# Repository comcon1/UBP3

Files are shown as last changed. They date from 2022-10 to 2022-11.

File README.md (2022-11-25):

# Universal Biopotential Amplifier - UBP3

Wideband multichannel differential amplifier with modular design and adjustable analogous commutation.

## Project video

Video presentation of the project (https://www.youtube.com/watch?v=Itqa7mGAqyA)

## Technical characteristics

- Input power: -15, 0, +15 V
- Type: differential
- Input resistance: 1 GOhm
- Noise level at connected inputs:
  - < 0.15 mkV (at 0.3-150 Hz)
  - < 0.8 mkV (at 0.3-1000 Hz)
- Gain coefficient:
  - Input cascade: 1, 10
  - Output cascade: 3, 10, 30, 100, 300, 1000
- Filtering:
  - Intensity: 12 dB/octave
  - LowPass: 35, 70, 150, 300, 1000, 2000, 5000, 10000, 20000 Hz 
  - HighPass: 0.1, 0.3, 1, 5, 20, 100, 300 Hz
- Output range: -5V - +5V

# Project structure

The amplifier is composed of two boards: **InputAmp** and **FilterAmp**. 

## InputAmp

Input gain board performs initial commutation of the bipolar signal with reference monopolar input and calibration signal. Next the board amplifies the signal current with 1x/10x gain.

Corresponding directory contains the complete KiCAD project including scheme and PCB.

## FilterAmp

Preamplified signal is then further amplified inside this board and undergo LowPass and HighPass filtration.

Corresponding directory contains the complete KiCAD project including scheme and PCB.

## Calibrator

Calibrator gets 0/+5V input unipolar source and gives 30/300 Hz of 1/0.1 mV square pulse unipolar signal for feeding the amplifier.

Corresponding directory contains the complete KiCAD project including scheme and PCB.

# Arrangement

Boards are designed for further geometrical stacking as shown at the how-to-assembly scheme:

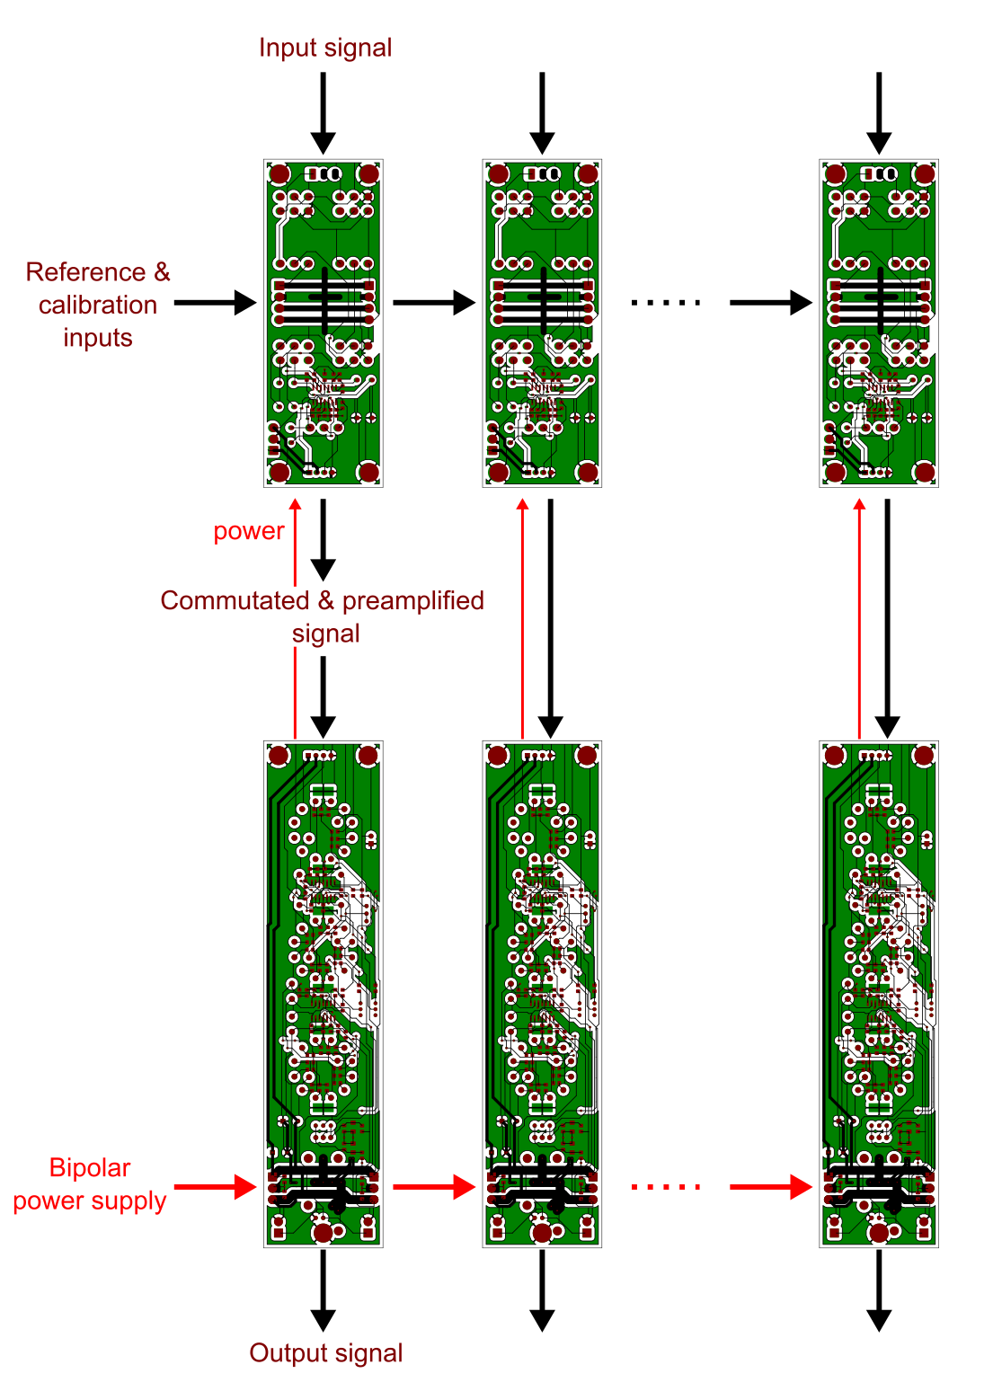
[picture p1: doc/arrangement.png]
How boards are assemblied


# History

The prototype of this amplifier was firstly used by Ilya Kuzmin and colleagues for recording ECG of rats on a tredban:

- Tarasova OS, Borzykh AA, Kuz'min IV, et al. [Dynamics of heart rate changes in rats following stepwise change of treadmill running speed]. Ross Fiziol Zh Im I M Sechenova. 2012; 98(11):1372-9.

Now it is used by Georgy Nikolaev and his students for recording EEG in the research of audiogenic epilepsy on rat model:

- Fedotova IB, Surina NM, Nikolaev GM, Revishchin AV, Poletaeva II. Rodent Brain Pathology, Audiogenic Epilepsy. Biomedicines. 2021; 9(11):1641. https://doi.org/10.3390/biomedicines9111641

# Licensing 

The project "Universal Biopotential Amplifier" 
(I. Kuzmin @kuzmin-ilya, A. Nesterenko @comcon1, G. Nikolaev)  
is released under  license CC BY-SA 3.0.

Submodules listed as independent projects are not part of this project and 
are released under their own licenses.

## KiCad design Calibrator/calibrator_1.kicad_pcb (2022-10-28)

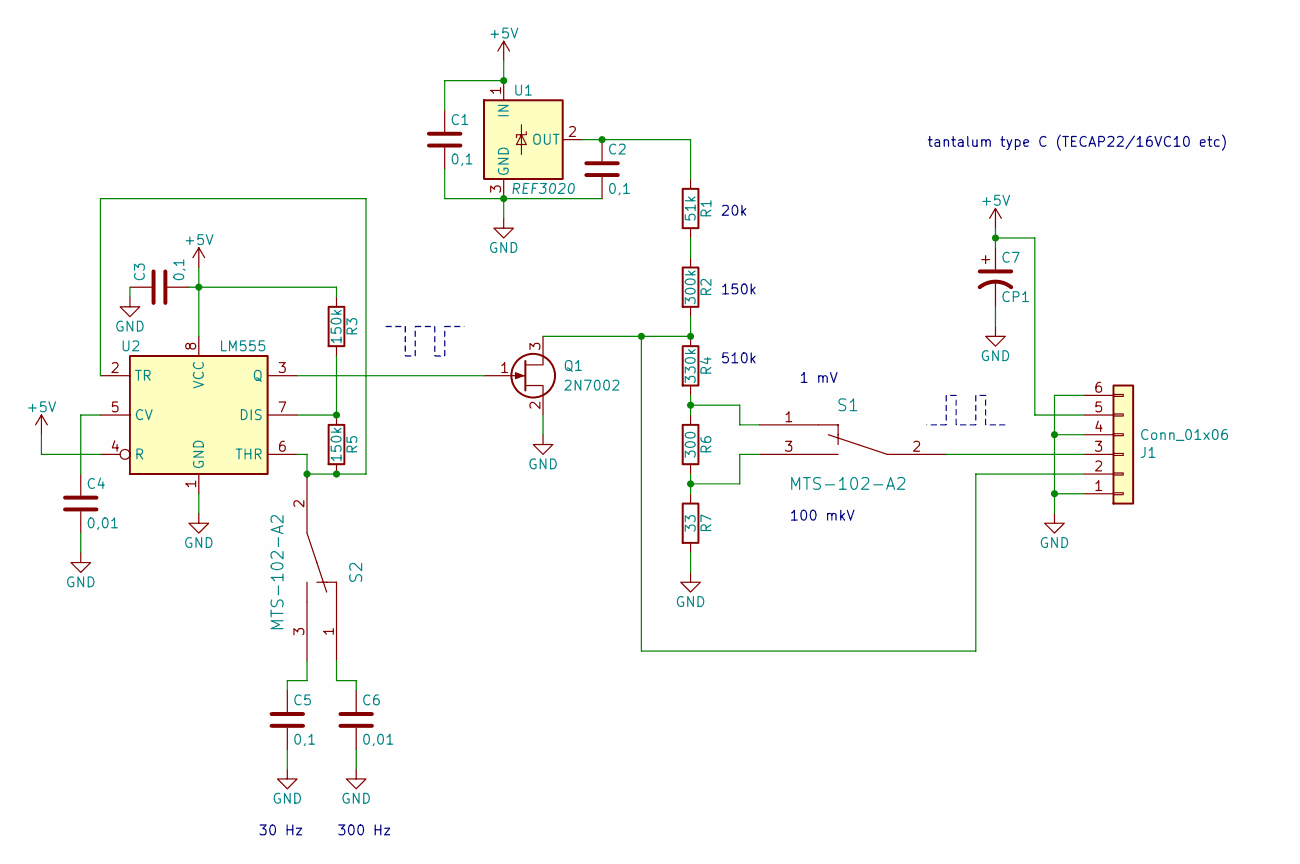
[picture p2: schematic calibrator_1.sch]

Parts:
C1, C2, C3, C5: 0,1; C_0805_2012Metric_Pad1.15x1.40mm_HandSolder
C4, C6: 0,01; C_0805_2012Metric_Pad1.15x1.40mm_HandSolder
C7: CP1; CP_EIA-6032-28_Kemet-C_Pad2.25x2.35mm_HandSolder
J1: Conn_01x06; PinHeader_1x06_P2.54mm_Horizontal
Q1: 2N7002; SOT-23_Handsoldering
R1: 51k; R_0805_2012Metric_Pad1.15x1.40mm_HandSolder
R2: 300k; R_0805_2012Metric_Pad1.15x1.40mm_HandSolder
R3, R5: 150k; R_0805_2012Metric_Pad1.15x1.40mm_HandSolder
R4: 330k; R_0805_2012Metric_Pad1.15x1.40mm_HandSolder
R6: 300; R_0805_2012Metric_Pad1.15x1.40mm_HandSolder
R7: 33; R_0805_2012Metric_Pad1.15x1.40mm_HandSolder
S1, S2: MTS-102-A2
U1: REF3020; SOT-23_Handsoldering
U2: LM555; SOIC-8_3.9x4.9mm_P1.27mm

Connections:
+5V: C1.1, C3.2, C7.1, J1.5, R3.1, U1.1 (IN), U2.4 (R), U2.8 (VCC)
GND: C1.2, C2.2, C3.1, C4.2, C5.2, C6.2, C7.2, J1.1, J1.4, J1.6, Q1.2 (S), R7.2, U1.3 (GND), U2.1 (GND)
unnamed: C2.1, R1.1, U1.2 (OUT)
unnamed: C4.1, U2.5 (CV)
unnamed: C5.1, S2.3
unnamed: C6.1, S2.1
unnamed: J1.2, Q1.3 (D), R2.2, R4.1
unnamed: J1.3, S1.2
unnamed: Q1.1 (G), U2.3 (Q)
unnamed: R1.2, R2.1
unnamed: R3.2, R5.1, U2.7 (DIS)
unnamed: R4.2, R6.1, S1.1
unnamed: R5.2, S2.2, U2.2 (TR), U2.6 (THR)
unnamed: R6.2, R7.1, S1.3

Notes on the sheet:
30 Hz
300 Hz
1 mV
100 mkV
tantalum type C (TECAP22/16VC10 etc)
510k
150k
20k

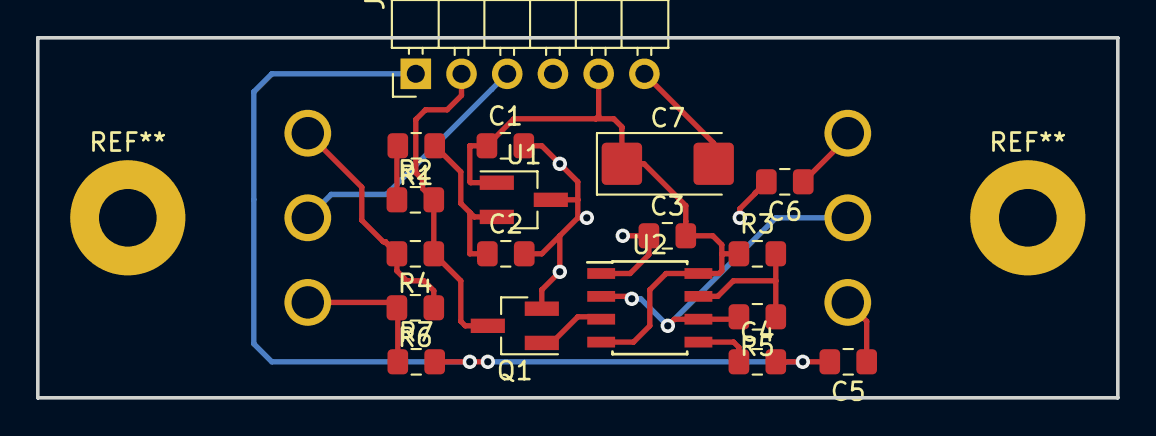
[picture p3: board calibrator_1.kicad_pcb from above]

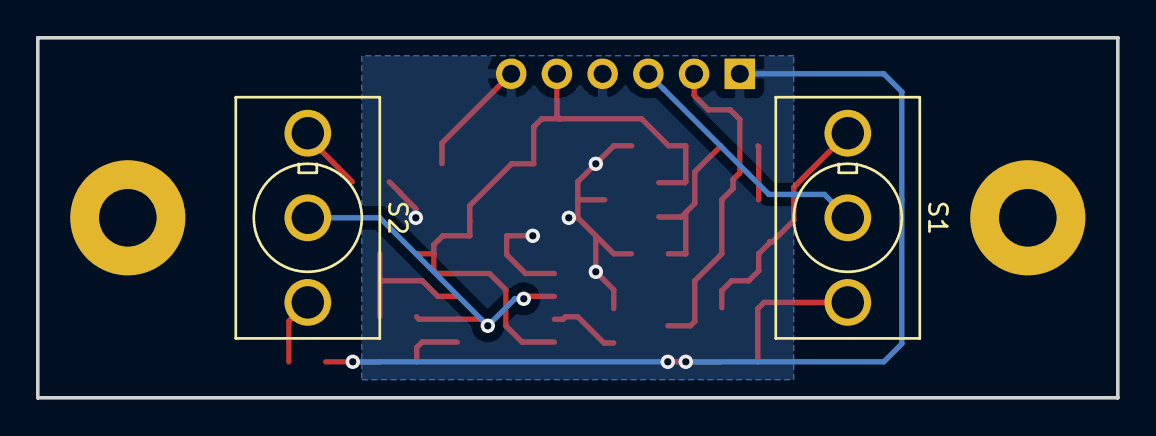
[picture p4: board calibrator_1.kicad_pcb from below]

Board: 2 copper layers, 60.0 x 20.0 mm, 20 parts (2 on the bottom side), 14 nets.

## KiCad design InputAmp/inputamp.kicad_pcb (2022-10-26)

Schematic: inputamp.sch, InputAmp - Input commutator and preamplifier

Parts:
C1, C2, C5: 1,0; C_Rect_L7.5mm_W6.5mm_P5.00mm
C3, C4: 0,1; C_0805_2012Metric_Pad1.18x1.45mm_HandSolder
J1: Conn_01x04; PinHeader_1x04_P2.54mm_Vertical
J2: Conn_01x03; PhoenixContact_MCV_1,5_3-G-3.81_1x03_P3.81mm_Vertical
J3, J5: Conn_01x04; SolderWirePad_1x04_P3.81mm_Drill1.2mm
J4: Conn_01x03; SolderWirePad_1x03_P3.81mm_Drill1.2mm
R1, R2: 20M; R_Axial_DIN0309_L9.0mm_D3.2mm_P12.70mm_Horizontal
R3: 7,5k; R_0805_2012Metric_Pad1.20x1.40mm_HandSolder
R4, R5, R6, R7, R8, R9: 30k; R_0805_2012Metric_Pad1.20x1.40mm_HandSolder
R10: 2M; R_0805_2012Metric_Pad1.20x1.40mm_HandSolder
R11: 33k; R_0805_2012Metric_Pad1.20x1.40mm_HandSolder
R12: 300k; R_0805_2012Metric_Pad1.20x1.40mm_HandSolder
SW1, SW2: MTS-202-A2; MTS-202-A2_odd_even
SW3, SW5, SW6: MTS-102-A2
SW4, SW7: MTS-212-A2; MTS-202-A2_odd_even
U1: TLC2274; SOIC-14_3.9x8.7mm_P1.27mm

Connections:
+5V: C3.2, J1.1, J4.1, U1.4
-5V: C4.2, J1.2, J4.3, U1.11
GND: C3.1, C4.1, J1.4, J2.2, J3.2, J4.2, J5.2, R1.2, R2.2, R8.2, R10.2, R11.2, SW1.5 (C), SW4.5 (C), SW7.6 (C)
unnamed: C1.1, R1.1, SW2.3 (B), U1.3
unnamed: C1.2, SW1.3 (B), SW2.1 (A)
unnamed: C2.1, R2.1, SW2.4 (B), U1.5
unnamed: C2.2, SW1.4 (B), SW2.2 (A)
unnamed: C5.1, R10.1, U1.12
unnamed: C5.2, R9.1, SW3.1, U1.8
unnamed: J1.3, SW3.2
unnamed: J2.1, SW7.2 (A)
unnamed: J2.3, SW4.1 (A)
unnamed: J3.1, J5.1, SW5.3, SW6.3
unnamed: J3.3, J5.3, SW1.6 (C)
unnamed: J3.4, J5.4, SW4.4 (B), SW7.3 (B)
unnamed: R3.1, R4.2, U1.2
unnamed: R3.2, R5.2, U1.6
unnamed: R4.1, R6.2, U1.1
unnamed: R5.1, R7.2, U1.7
unnamed: R6.1, R9.2, U1.9
unnamed: R7.1, R8.1, U1.10
unnamed: R11.1, R12.2, U1.13
unnamed: R12.1, SW3.3, U1.14
unnamed: SW1.1 (A), SW5.2
unnamed: SW1.2 (A), SW6.2
unnamed: SW4.3 (B), SW6.1, SW7.5 (C)
unnamed: SW4.6 (C), SW5.1, SW7.4 (B)

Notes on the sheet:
x10
CAL
ShieldGND
C1, C2, C5 - Epcos B32529C0105K000
Output connector (to "filteramp" block)
Reserve connector to supply power for input devices
Signal input connector
IN- GND IN+
LowPass frequency is about 0.1 Hz
SIG_OUT GND
REF
Rin
CAL_R
"CAL_R": to the +1V output of the calibrator through 1 MOhm "CAL": directly to the +1mV output of the calibrator "REF": when the circuite works in a stack, one of the inputs (called REF) is connected to all boards and may replace + or - inputs "ShieldGND": connect the shield of REF wire and DON'T c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
Connect to J5 of the next board in a stack. DON'T connect ShieldGND between boards!

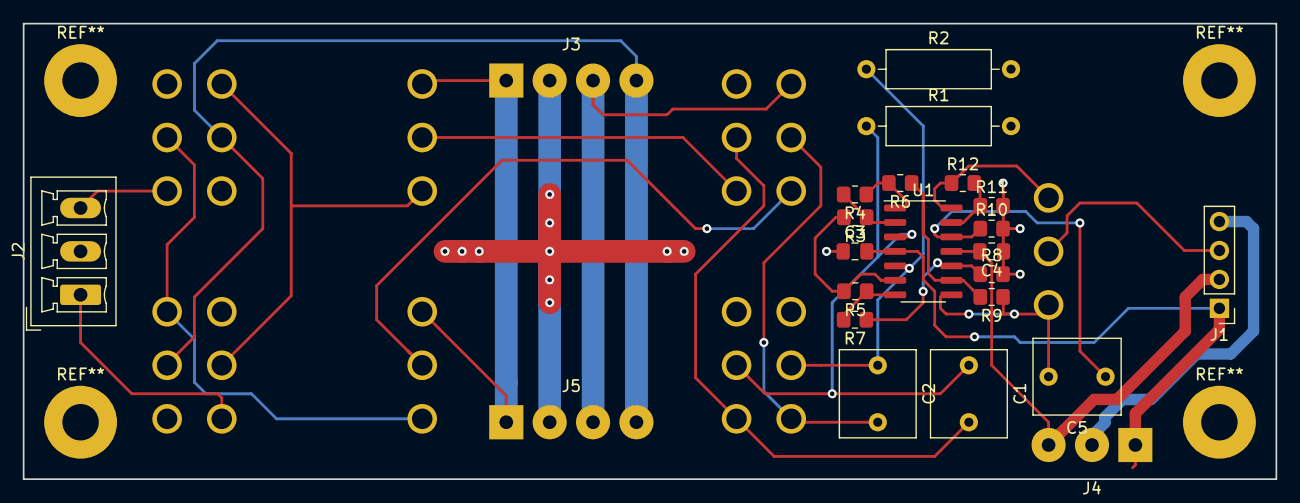
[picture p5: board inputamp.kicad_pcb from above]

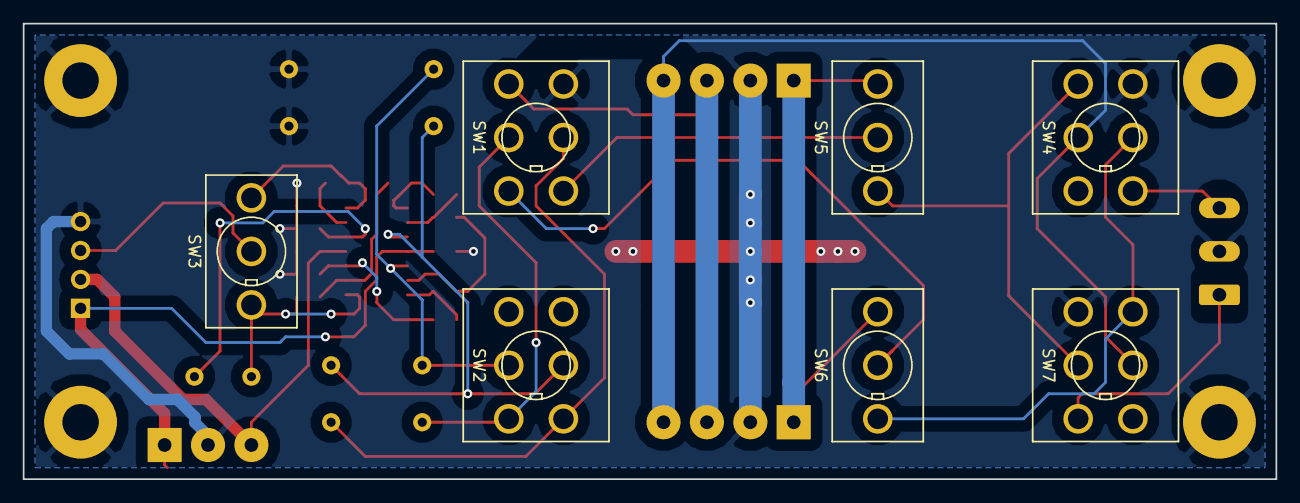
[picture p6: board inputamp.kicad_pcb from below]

Board: 2 copper layers, 110.0 x 40.0 mm, 30 parts (7 on the bottom side), 27 nets.

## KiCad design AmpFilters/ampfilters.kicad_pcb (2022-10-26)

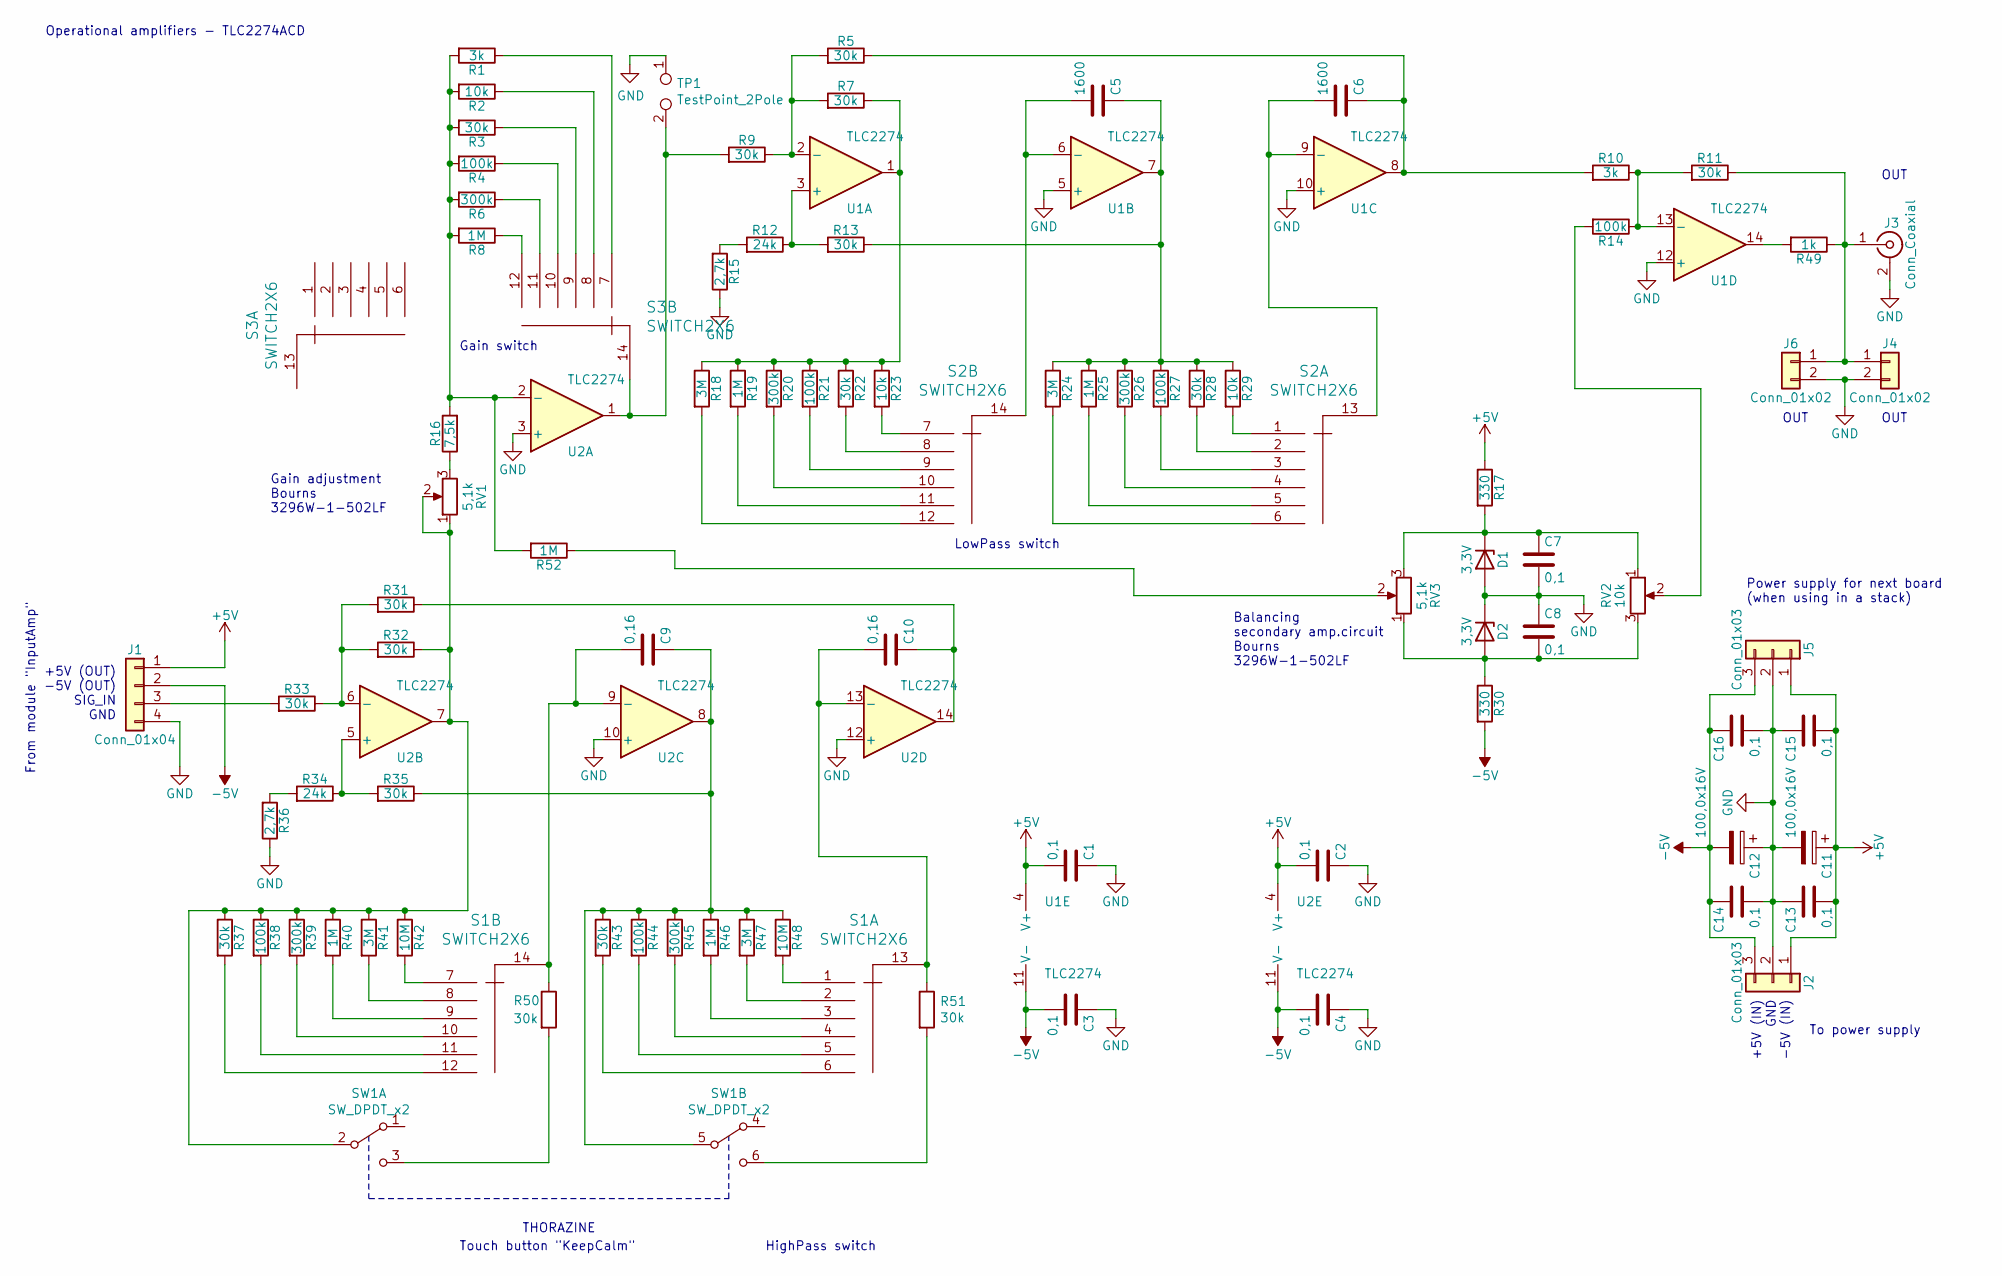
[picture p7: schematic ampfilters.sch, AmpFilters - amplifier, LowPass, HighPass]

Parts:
C1, C2, C3, C4, C7, C8, C13, C14, C15, C16: 0,1; C_0805_2012Metric_Pad1.18x1.45mm_HandSolder
C5, C6: 1600; 71-7small
C9, C10: 0,16; 71-7big
C11, C12: 100,0x16V; CP_Radial_D8.0mm_P5.00mm
D1, D2: 3,3V; D_1206_3216Metric_Pad1.42x1.75mm_HandSolder
J1: Conn_01x04; PinHeader_1x04_P2.54mm_Vertical
J2, J5: Conn_01x03; SolderWirePad_1x03_P3.81mm_Drill1.2mm
J3: Conn_Coaxial; BNC-7043
J4, J6: Conn_01x02; SolderWirePad_1x02_P3.81mm_Drill1.2mm
R1, R10: 3k; R_0805_2012Metric_Pad1.20x1.40mm_HandSolder
R2, R23, R29: 10k; R_0805_2012Metric_Pad1.20x1.40mm_HandSolder
R3, R5, R7, R9, R11, R13, R22, R28, R31, R32, R33, R35, R37, R43, R50, R51: 30k; R_0805_2012Metric_Pad1.20x1.40mm_HandSolder
R4, R14, R21, R27, R38, R44: 100k; R_0805_2012Metric_Pad1.20x1.40mm_HandSolder
R6, R20, R26, R39, R45: 300k; R_0805_2012Metric_Pad1.20x1.40mm_HandSolder
R8, R19, R25, R40, R46, R52: 1M; R_0805_2012Metric_Pad1.20x1.40mm_HandSolder
R12, R34: 24k; R_0805_2012Metric_Pad1.20x1.40mm_HandSolder
R15, R36: 2,7k; R_0805_2012Metric_Pad1.20x1.40mm_HandSolder
R16: 7,5k; R_0805_2012Metric_Pad1.20x1.40mm_HandSolder
R17, R30: 330; R_0805_2012Metric_Pad1.20x1.40mm_HandSolder
R18, R24, R41, R47: 3M; R_0805_2012Metric_Pad1.20x1.40mm_HandSolder
R42, R48: 10M; R_0805_2012Metric_Pad1.20x1.40mm_HandSolder
R49: 1k; R_0805_2012Metric_Pad1.20x1.40mm_HandSolder
RV1, RV3: 5,1k; Potentiometer_Bourns_3296W_Vertical
RV2: 10k; POT_VERT
S1, S2, S3: SWITCH2X6; SR25P-1-2-6_mirrored
SW1: SW_DPDT_x2; PS700
TP1: TestPoint_2Pole; PinHeader_1x02_P2.54mm_Vertical
U1, U2: TLC2274; SOIC-14_3.9x8.7mm_P1.27mm

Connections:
+5V: C1.2, C2.2, C11.1, C13.2, C15.2, J1.1, J2.1, J5.1, R17.1, U1.4 (V+), U2.4 (V+)
-5V: C3.2, C4.2, C12.2, C14.1, C16.1, J1.2, J2.3, J5.3, R30.2, U1.11 (V-), U2.11 (V-)
GND: C1.1, C2.1, C3.1, C4.1, C7.2, C8.1, C11.2, C12.1, C13.1, C14.2, C15.1, C16.2, D1.2 (A), D2.1 (K), J1.4, J2.2, J3.2 (Ext), J4.2, J5.2, J6.2, R15.1, R36.1, TP1.1, U1.5 (+), U1.10 (+), U1.12 (+), U2.3 (+), U2.10 (+), U2.12 (+)
unnamed: C5.1, R13.1, R24.1, R25.1, R26.1, R27.1, R28.1, R29.1, U1.7
unnamed: C5.2, S2.14, U1.6 (-)
unnamed: C6.1, R5.1, R10.2, U1.8
unnamed: C6.2, S2.13, U1.9 (-)
unnamed: C7.1, D1.1 (K), R17.2, RV2.1, RV3.3
unnamed: C8.2, D2.2 (A), R30.1, RV2.3, RV3.1
unnamed: C9.1, R35.1, R43.1, R44.1, R45.1, R46.1, R47.1, R48.1, SW1.5 (B), U2.8
unnamed: C10.1, R31.1, U2.14
unnamed: J1.3, R33.2
unnamed: J3.1 (In), J4.1, J6.1, R11.1, R49.1
unnamed: R1.1, S3.7
unnamed: R1.2, R2.2, R3.2, R4.2, R6.2, R8.2, R16.2, R52.2, U2.2 (-)
unnamed: R2.1, S3.8
unnamed: R3.1, S3.9
unnamed: R4.1, S3.10
unnamed: R5.2, R7.2, R9.1, U1.2 (-)
unnamed: R6.1, S3.11
unnamed: R8.1, S3.12
unnamed: R9.2, S3.14, TP1.2, U2.1
unnamed: R10.1, R11.2, R14.1, U1.13 (-)
unnamed: R12.1, R13.2, U1.3 (+)
unnamed: R12.2, R15.2
unnamed: R14.2, RV2.2
unnamed: R16.1, RV1.3
unnamed: R7.1, R18.1, R19.1, R20.1, R21.1, R22.1, R23.1, U1.1
unnamed: R18.2, S2.12
unnamed: R19.2, S2.11
unnamed: R20.2, S2.10
unnamed: R21.2, S2.9
unnamed: R22.2, S2.8
unnamed: R23.2, S2.7
unnamed: R24.2, S2.6
unnamed: R25.2, S2.5
unnamed: R26.2, S2.4
unnamed: R27.2, S2.3
unnamed: R28.2, S2.2
unnamed: R29.2, S2.1
unnamed: R31.2, R32.2, R33.1, U2.6 (-)
unnamed: R32.1, R37.1, R38.1, R39.1, R40.1, R41.1, R42.1, RV1.1, RV1.2, SW1.2 (B), U2.7
unnamed: R34.1, R35.2, U2.5 (+)
unnamed: R34.2, R36.2
unnamed: R37.2, S1.12
unnamed: R38.2, S1.11
unnamed: R39.2, S1.10
unnamed: R40.2, S1.9
unnamed: R41.2, S1.8
unnamed: R42.2, S1.7
unnamed: R43.2, S1.6
unnamed: R44.2, S1.5
unnamed: R45.2, S1.4
unnamed: R46.2, S1.3
unnamed: R47.2, S1.2
unnamed: R48.2, S1.1
unnamed: R49.2, U1.14
unnamed: R50.2, SW1.3 (C)
unnamed: R51.2, SW1.6 (C)
unnamed: R52.1, RV3.2

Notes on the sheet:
THORAZINE
Gain adjustment Bourns 3296W-1-502LF
OUT
Balancing secondary amp.circuit Bourns 3296W-1-502LF
Gain switch
+5V (IN) GND -5V (IN)
+5V (OUT) -5V (OUT) SIG_IN GND
Touch button "KeepCalm"
From module "InputAmp"
To power supply
Operational amplifiers - TLC2274ACD
HighPass switch
LowPass switch
Power supply for next board (when using in a stack)

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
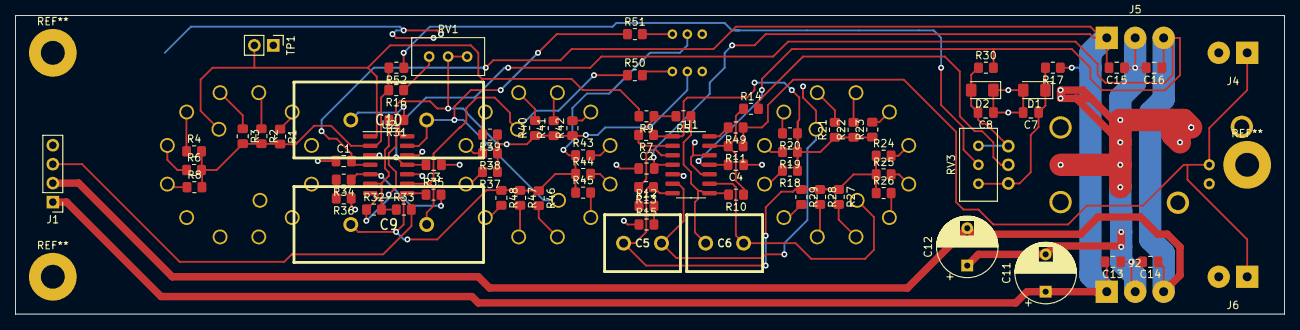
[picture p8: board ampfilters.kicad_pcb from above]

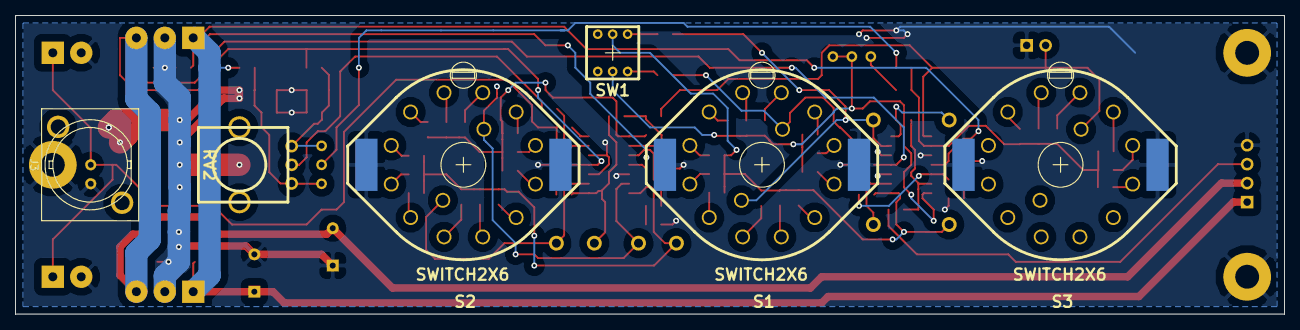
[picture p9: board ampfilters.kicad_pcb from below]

Board: 2 copper layers, 170.0 x 40.0 mm, 86 parts (6 on the bottom side), 62 nets.

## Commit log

2022-10-26 firstly add main circuits and associated files
    [ampfilters.kicad_pcb, ampfilters.sch, inputamp.kicad_pcb, inputamp.sch]
2022-10-28 Add Calibrator board to the project
    [calibrator_1.kicad_pcb, calibrator_1.sch]
2022-11-25 insert video from GOSH and history to README
